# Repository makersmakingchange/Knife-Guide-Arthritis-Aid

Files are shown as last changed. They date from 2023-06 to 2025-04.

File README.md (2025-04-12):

# Knife Guide Arthritis Aid
The Knife Guide Arthritis Aid is a handle that attached to the back of a knife that allows a user to use both hands and requires less grip strength for the same amount of control. It is designed for users with arthritis that have difficulty gripping the handles of knives.

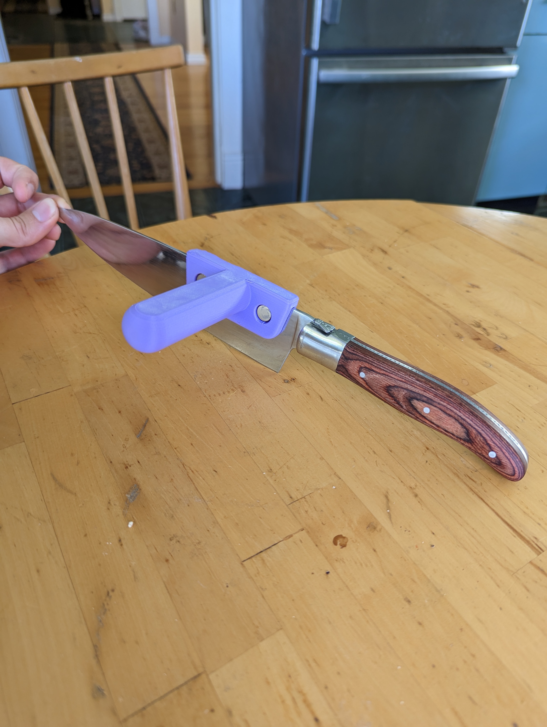
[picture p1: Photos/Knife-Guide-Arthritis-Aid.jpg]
Picture of Knife Guide Arthritis Aid.


## More info at
- [Makers Making Change Project Page](https://makersmakingchange.com/project/knife-guide-arthritis-aid/)

## How to Obtain a Knife Guide Arthritis Aid
### 1. Do it Yourself (DIY) or Do it Together (DIT)

This is an open-source assistive technology, so anyone is free to build it. All of the files and instructions required to build the Knife Guide Arthritis Aid are contained within this repository. Refer to the Maker Checklist below.

### 2. Request a build of this device

If you would like to obtain a Knife Guide Arthritis Aid, you may submit a build request through the [MMC Library Page](https://makersmakingchange.com/project/knife-guide-arthritis-aid/). The requestor is responsible for the cost of materials and any shipping.

### 3. How to build this device for someone else

If you have the skills and equipment to build this device, and would like to donate your time to create the switch for someone who needs it, visit the [MMC Maker Wanted](https://makersmakingchange.com/maker-wanted/) section.

## Getting Started

### 1. Read the Makers Checklist

The Makers Checklist 

### 2. Order the Off-The-Shelf Components

The [Bill of Materials](/Documentation/Knife_Guide_Arthritis_Aid_BOM_V1.0.xlsx) lists all of the parts and components required to build the Knife Guide Arthritis Aid. The of the off-the-shelf components are online or may be available in smaller quantities at your local hardware store or dollar store.

### 3. Print the 3D Printable components

Print the components

All of the files and individual print files can be in the [/Build_Files/3D_Printing_Files](/Build_Files/3D_Printing_Files/) folder.

### 4. Assemble the Knife Guide Arthritis Aid

Reference the [Assembly Guide](/Documentation/Knife_Guide_Arthritis_Aid_Assembly_Guide_V1.0.pdf) for the tools and steps required to build each portion.

## Files
### Documentation
| Document             | Version | Link |
|----------------------|---------|------|
| Design Rationale     | 1.0     | [Knife_Guide_Arthritis_Aid_Design_Rationale](/Documentation/Knife_Guide_Arthritis_Aid_Design_Rationale_V1.0.pdf)     |
| Maker Checklist      | 1.0     | [Knife_Guide_Arthritis_Aid_Maker_Checklist](/Documentation/Knife_Guide_Arthritis_Aid_Maker_Checklist_V1.0.pdf)     |
| Bill of Materials    | 1.0     | [Knife_Guide_Arthritis_Aid_Bill_of_Materials](/Documentation/Knife_Guide_Arthritis_Aid_BOM_V1.0.xlsx)     |
| 3D Printing Guide    | 1.0     | [Knife_Guide_Arthritis_Aid_3D_Printing_Guide](/Documentation/Knife_Guide_Arthritis_Aid_3D_Printing_Guide_V1.0.pdf)     |
| Assembly Guide       | 1.0     | [Knife_Guide_Arthritis_Aid_Assembly_Guide](/Documentation/Knife_Guide_Arthritis_Aid_Assembly_Guide_V1.0.pdf)     |
| User Guide           | 1.0     | [Knife_Guide_Arthritis_Aid_User_Guide](/Documentation/Knife_Guide_Arthritis_Aid_User_Guide_V1.0.pdf)    |
| Changelog            | 1.0     | [Knife_Guide_Arthritis_Aid_Changelog](/Documentation/Knife_Guide_Arthritis_Aid_Changelog_V1.0.pdf)     |

### Design Files
 - [CAD Files](/Design_Files)

### Build Files
 - [3D Printing Files](/Build_Files/3D_Printing_Files)

## Attribution
Designers:
 - Initial design by [Christopher Thormodson](https://www.myminifactory.com/users/cjthormodson)
 - Update design and documentation by Neil Squire Society / Makers Making Change. 

## License
Everything needed or used to design, make, test, or prepare the Knife Guide Arthritis Aid is licensed under the [MyMiniFactory - Credit - Remix - Noncommercial](https://www.myminifactory.com/object-licensing).

Accompanying material such as instruction manuals, videos, and other copyrightable works that are useful but not necessary to design, make, test, or prepare the Knife Guide Arthritis Aid are published under a Creative Commons Attribution-ShareAlike 4.0 license https://creativecommons.org/licenses/by-sa/4.0/ (CC BY-SA 4.0).

----

<!-- ABOUT MMC START -->
## About Makers Making Change
[Makers Making Change Logo](https://www.makersmakingchange.com/)

Makers Making Change is a program of [Neil Squire](https://www.neilsquire.ca/), a Canadian non-profit that uses technology, knowledge, and passion to empower people with disabilities.

Makers Making Change leverages the capacity of community based Makers, Disability Professionals and Volunteers to develop and deliver affordable Open Source Assistive Technologies.

 - Website: [www.MakersMakingChange.com](https://www.makersmakingchange.com/)
 - GitHub: [makersmakingchange](https://github.com/makersmakingchange)
 - Bluesky: [@makersmakingchange.bsky.social](https://bsky.app/profile/makersmakingchange.bsky.social)
 - Instagram: [@makersmakingchange](https://www.instagram.com/makersmakingchange)
 - Facebook: [makersmakechange](https://www.facebook.com/makersmakechange)
 - LinkedIn: [Neil Squire Society](https://www.linkedin.com/company/neil-squire-society/)
 - Thingiverse: [makersmakingchange](https://www.thingiverse.com/makersmakingchange/about)
 - Printables: [MakersMakingChange](https://www.printables.com/@MakersMakingChange)

### Contact Us
For technical questions, to get involved, or to share your experience we encourage you to [visit our website](https://www.makersmakingchange.com/) or [contact us](https://www.makersmakingchange.com/s/contact).
<!-- ABOUT MMC END -->

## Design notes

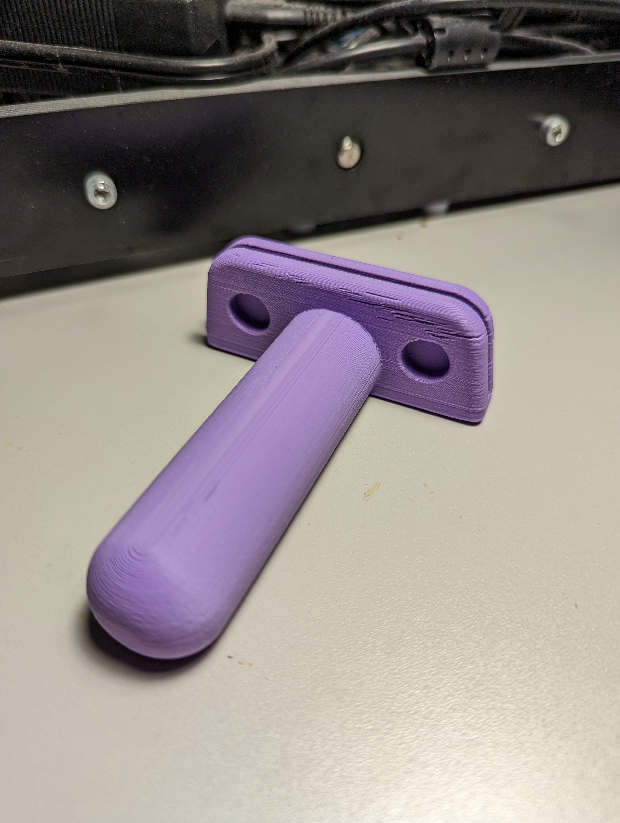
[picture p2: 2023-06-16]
Photos/One_Piece_Handle.jpg

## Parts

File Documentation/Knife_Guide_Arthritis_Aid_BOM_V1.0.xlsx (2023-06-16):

Device: xxxxx |  | Total Cost | Total Print time (hr) | Total filament (g)
Version: V1.0 | Date Created: 4/20/2021 | $1.93 | 3.37 | 27
Commercial Parts:
Part type (Electrical. Mechanical, Sanitization, ect) | Part Name | Quantity Needed | Pkg Quantity | Price per package | Price per Unit | Price for qty needed | Link
Mechanical | Magnet 15mmx3mm | 4 | 60 | $18.77 | $0.31 | $1.25 | https://www.amazon.ca/dp/B09DYG7GLW?psc=1&ref=ppx_yo2ov_dt_b_product_details
 |  |  |  |  |  | $0.00
 |  |  |  |  |  | $0.00
3D Printed Parts ESTIMATED PRICING USING 1KG ROLL COST: | $25.00
Part | Description | Quantity Needed | TOTAL Mass (g) | Estimated Price | Print Time (Min) | Link
One_Piece_Handle.stl | The main device handle | 1 | 27 | $0.68 | 202
 |  |  |  | $0.00
 |  |  |  | $0.00
 |  |  |  | $0.00
 |  |  |  | $0.00
 |  |  | Total Print Cost: | $0.68
Tools for Assembly
Superglue
Alternatives (if there are other sources for some parts link them below)
Part and description | Link

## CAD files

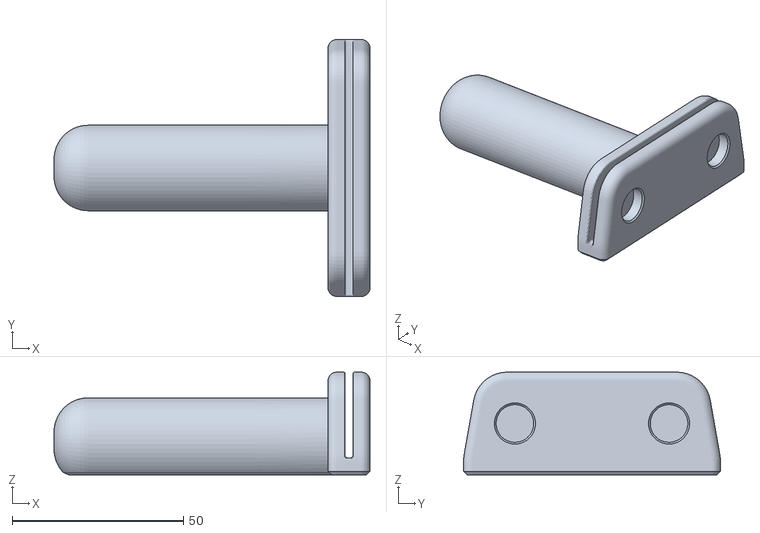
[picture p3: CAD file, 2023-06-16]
Build_Files/3D_Printing_Files/One_Piece_Handle.stl
92.2 x 75.0 x 30.0

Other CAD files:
Design_Files/One Piece Handle v3.f3d

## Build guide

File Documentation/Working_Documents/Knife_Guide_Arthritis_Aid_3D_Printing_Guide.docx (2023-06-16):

# 3D Printing Summary

Metrics
Total Print Time (min) | 202
Total Number of Components | 1
Typical Total Mass (g) | 27
Typical Number of Print Setups | 1

# 3D Printing Settings

Print File Name | Qty | Total Print Time (hr:min) | Mass (g) | Infill (%) | Support(Y/N) | Layer Height/ Nozzle Diameter(mm) | Notes (orientation, special settings, etc.)
One_Piece_Handle.stl | 1 | 3:22 | 27 | 20 | N | 0.2/0.4 | - Print in orientation given in STL

# Customization Options

- The device can be printed in any colour the user would like
- The width of the knife channel can be changed in the Fusion 360 file

# Examples of Quality Prints

Photos of One_Piece_Handle

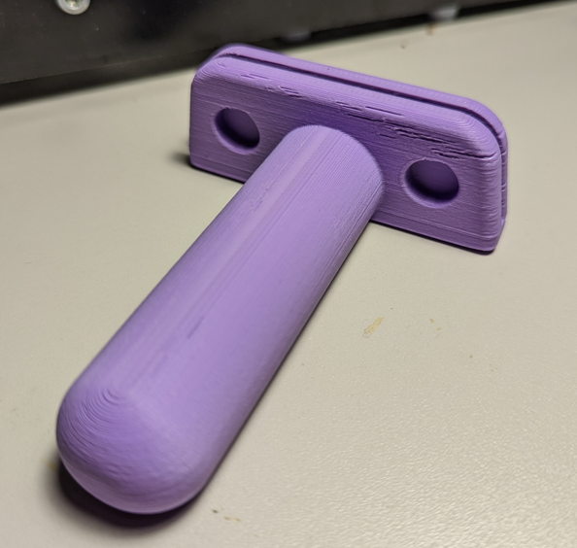
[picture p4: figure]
The one piece handle printed in purple

© 2023 by Neil Squire. This work is licensed under the CC BY SA 4.0 License: http://creativecommons.org/licenses/by-sa/4.0 Files available at https://makersmakingchange.com/project/knife-guide-arthritis-aid/ Page 1 of 2

V1.0 | March 2023 Knife Guide Arthritis Aid 3D Printing Guide

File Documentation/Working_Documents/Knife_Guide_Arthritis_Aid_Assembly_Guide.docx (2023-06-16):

# Required Components

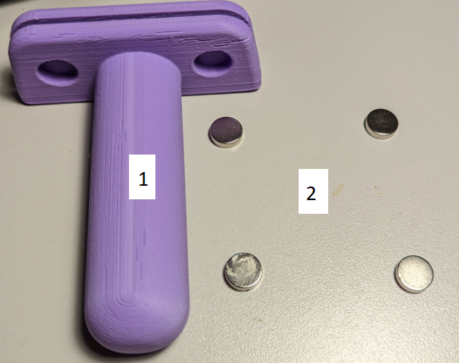
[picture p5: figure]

| BOM 1. One_Piece_Handle.stl x1 2. Magnet x4

# Required Tools

- Gorilla Glue

# Required Personal Protective Equipment (PPE)

- Safety glasses

# Assembly Instructions

## Step 1

Take 4 magnets and place them into the slots on the 3D printed handle. The magnets will hold themselves in place. Using a pea sized amount of gorilla glue, secure the magnets in place so they cannot be removed.

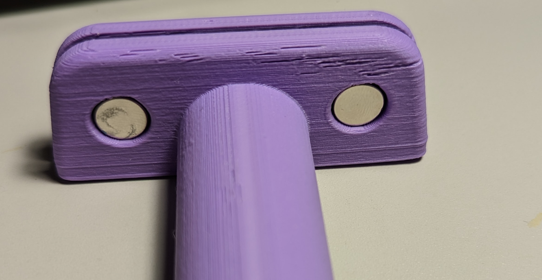
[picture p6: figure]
Printed device with the magnets installed

## Step 2

Place the assembled handle over the spine of the knife to complete the build.

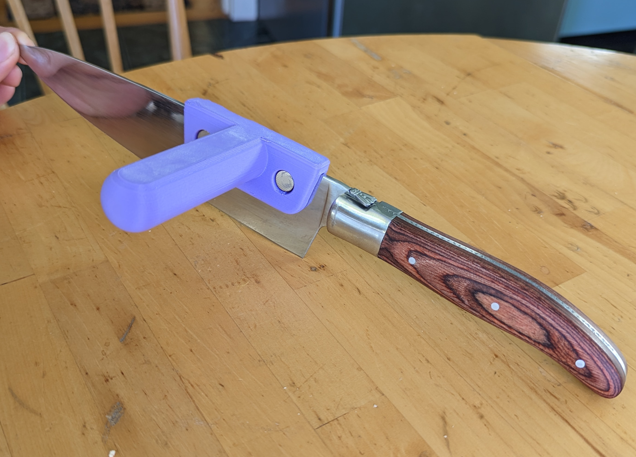
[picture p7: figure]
A chefs knife with the assembled device sitting on the spine of the knife, near the handle

© 2023 by Neil Squire. This work is licensed under the CC BY SA 4.0 License: http://creativecommons.org/licenses/by-sa/4.0 Files available at https://makersmakingchange.com/project/knife-guide-arthritis-aid/ Page 1 of 1

V1.0 | March 2023 Knife Guide Arthritis Aid Assembly Guide

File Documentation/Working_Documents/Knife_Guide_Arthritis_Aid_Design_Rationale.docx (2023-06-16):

# Introduction

The Knife Guide Arthritis Aid is a handle that attached to the back of a knife that allows a user to use both hands and requires less grip strength for the same amount of control. It is designed for users with arthritis that have difficulty gripping the handles of knives.

# Research

Name | Image | Price | Link

Commercial

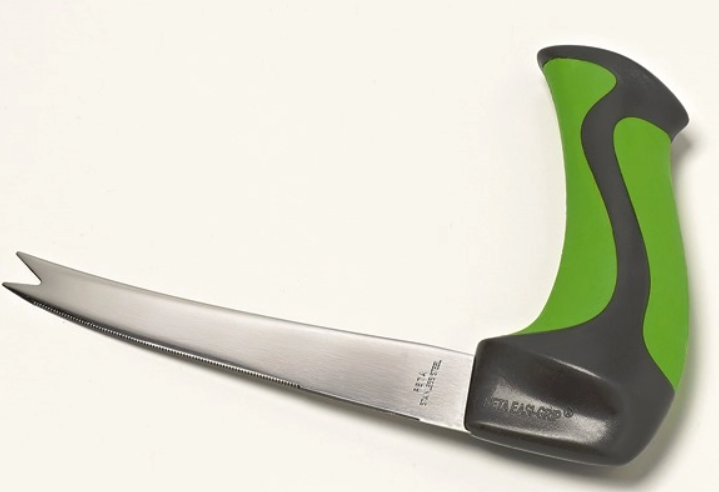
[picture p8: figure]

Easi-Grip Arthritis Fork Knife | | $17.95 | Link (https://www.arthritissupplies.com/easi-grip-arthritis-fork-knife.html)

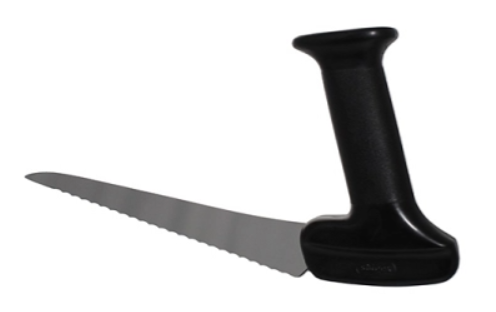
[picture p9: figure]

Swedish Serrated Knife | | $45.95 | Link (https://www.arthritissupplies.com/swedish-serrated-knife.html)

DIY

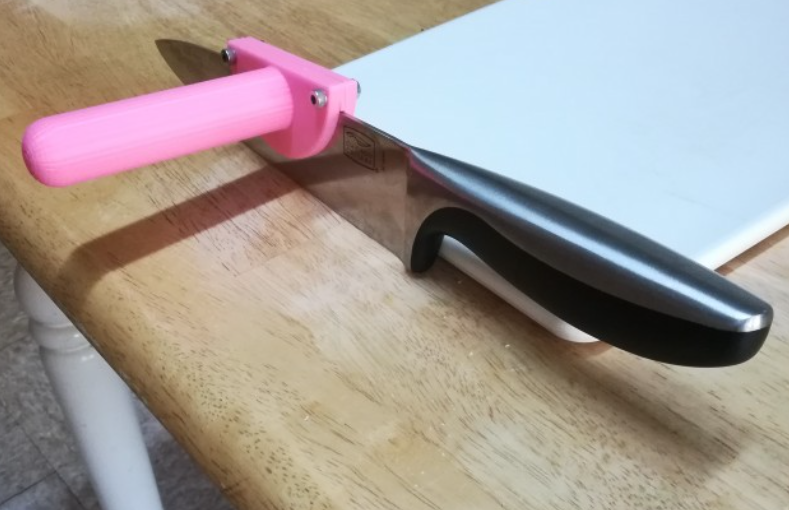
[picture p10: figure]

3D Printable Knife Guide Arthritis Aid | | N/A | Link (https://www.myminifactory.com/object/3d-print-knife-guide-arthritis-aid-77506)

# Requirements

## Goals

G01 | Create a handle that allows arthritis uses to use a knife

## Functional Requirements

F01 | Device must firmly hold onto the knife
F02 | Device must have a more natural grip position
F03 | Device must not block use of the knife

## Constraints

C01 | Device must be printed in one piece with no supports

# Prototyping

Version 1: Original Design

- Two flat plates with a spacer between them, connected by two bolts with a handle on one plate
- When the screws are tightened, the plates angle and separate at the bottom, preventing them from gripping the blade

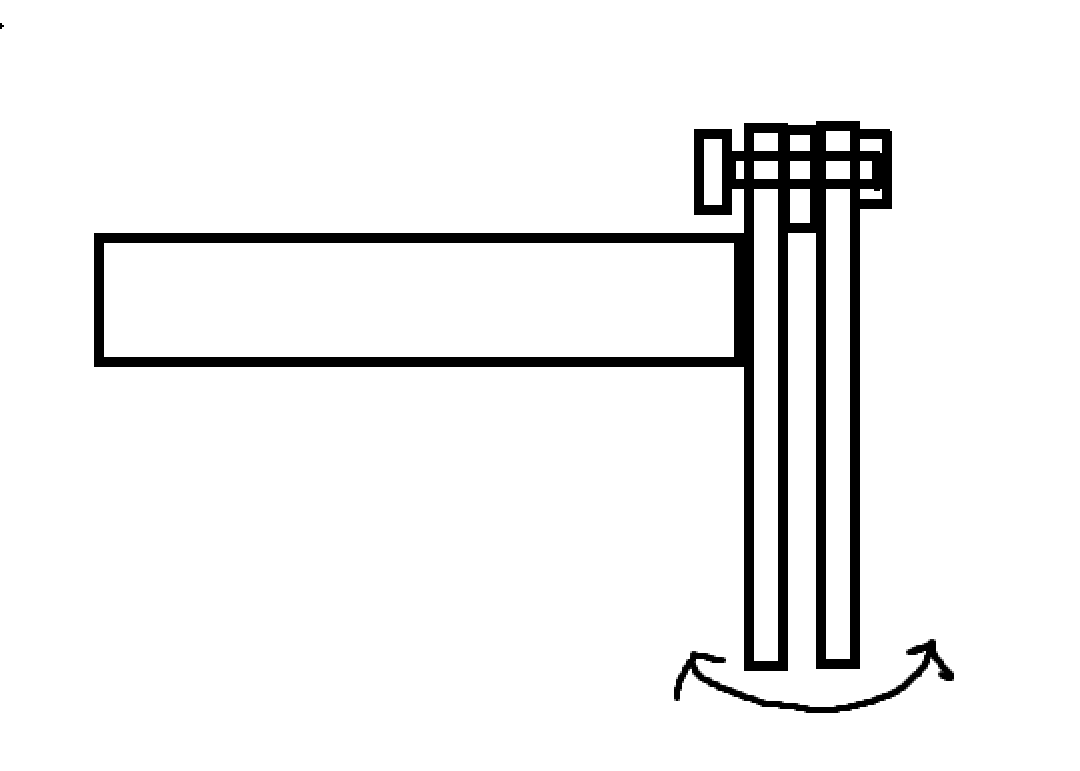
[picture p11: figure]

Version 2: Modified Design

- The plates were modified so they had a taper that would keep the plates parallel after the screws are tightened
- The plates still were loose after the screws were tightened

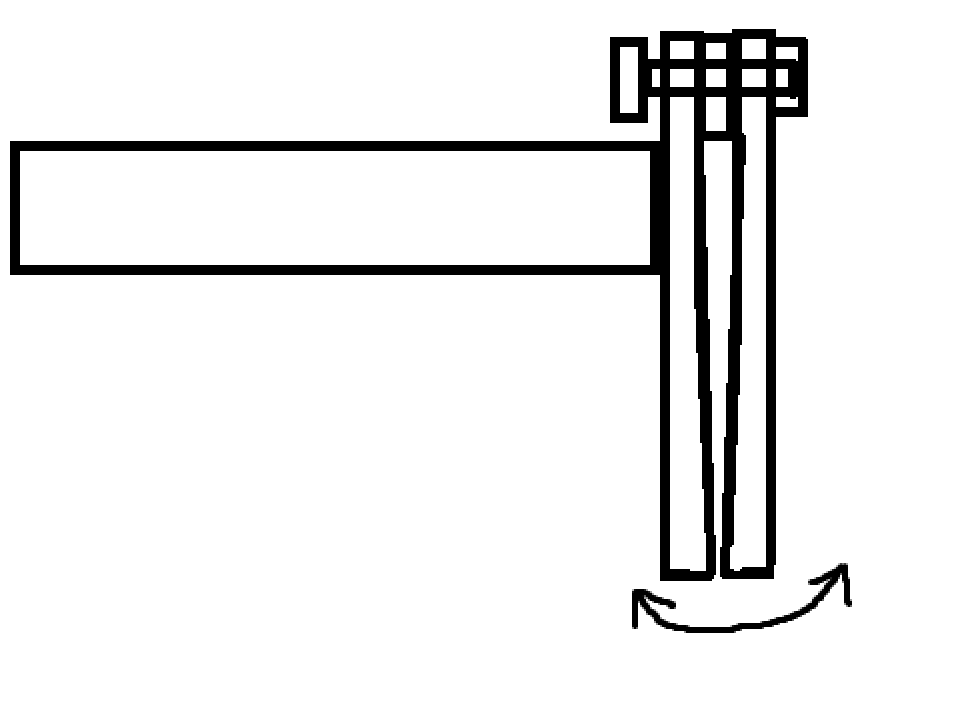
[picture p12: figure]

Version 3: Magnet Design

- One piece print in place design
- Pockets for magnets to be inserted on the outside
- Knife thickness is a parametric variable that can be changed
- Most force is on the downstroke, the magnets keep the handle on the knife on the upstroke, but not expected to have to bear significant force
- Covers much less of the blade, allowing it to be used on non-chef knives

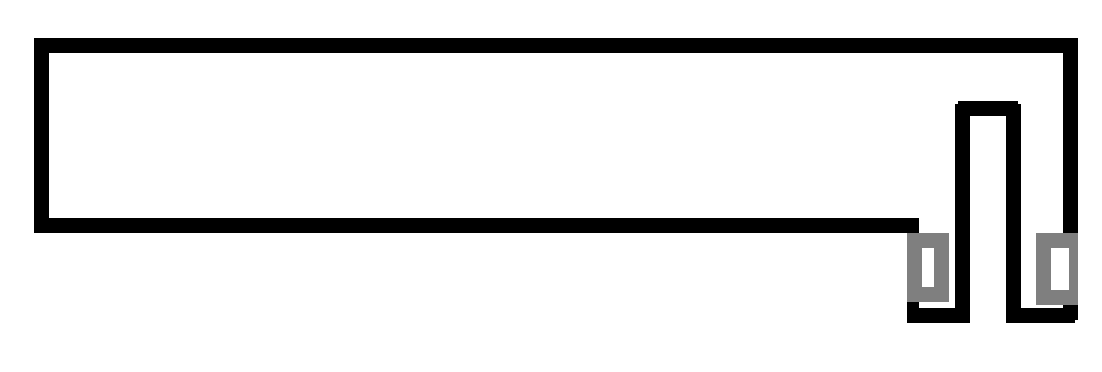
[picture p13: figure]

# Testing

After assembling the final magnet version, it was found to stay on the knife well, and it left a usable amount of the knife exposed. Gorilla glue was chosen as the glue, since it is food safe, as well as being less brittle to resist the shock of being dropped.

# Opportunities for Improvement

The handle could be rotated 90 degrees to be vertical, as seen on some commercial arthritis knives.

© 2023 by Neil Squire. This work is licensed under the CC BY SA 4.0 License: http://creativecommons.org/licenses/by-sa/4.0 Files available at https://makersmakingchange.com/project/knife-guide-arthritis-aid/ Page 1 of 1

V1.0 | March 2023 Knife Guide Arthritis Aid Design Rationale

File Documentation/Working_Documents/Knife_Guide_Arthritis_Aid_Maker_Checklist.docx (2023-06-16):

# Maker To Do List

- Read through the Assembly Guide to become familiar with required components, tools, supplies, and safety gear and overall assembly steps.
- Talk to User about customization options (e.g., color, any special requests, etc.)
- Order hardware components
- Gather tools, supplies, and safety equipment.
- Assemble the device
- Test device
- Print “User Quick Guide”

# Items to Give to User

- Assembled, tested device
- “User Quick Guide”

© 2023 by Neil Squire. This work is licensed under the CC BY SA 4.0 License: http://creativecommons.org/licenses/by-sa/4.0 Files available at https://makersmakingchange.com/project/knife-guide-arthritis-aid/ Page 1 of 1

V1.0 | March 2023 Knife Guide Arthritis Aid Maker Checklist

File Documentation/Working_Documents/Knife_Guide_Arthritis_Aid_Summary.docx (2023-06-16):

# Title

Knife Guide Arthritis Aid

## Subtitle

The Knife Guide Arthritis Aid is a handle that attached to the back of a knife that allows a user to use both hands and requires less grip strength for the same amount of control.

## Device Details

### Overview

The Knife Guide Arthritis Aid is a handle that attached to the back of a knife that allows a user to use both hands and requires less grip strength for the same amount of control. It is designed for users with arthritis that have difficulty gripping the handles of knives.

### Usage

To use, place the device over the back of the knife. The new handle can now be gripped at a more natural angle than the original handle, and the knife used as normal. However, at least one hand must remain on the original handle during use. Attempting to hold the knife with just the new handle could cause the knife to fall out of the handle.

### Cost

<$5

### Build Instructions

<Summary of build – off-the shelf parts? Custom PCB? 3D Printing? Programming?

#### Skills Required

- 3D printing

#### Time Required

3D printing time: 3h 22min

Assembly Time: 5 min

#### Tools

- 3D printer
- Superglue

#### Components

- 1x One_Piece_Handle.stl
- 4x magnet

### Attribution

- Initial design by Christopher Thormodson @cjthormodson - MyMiniFactory (https://www.myminifactory.com/users/cjthormodson)
- Revisions and documentation by Neil Squire Society/Makers Making Change

© 2023 by Neil Squire. This work is licensed under the CC BY SA 4.0 License: http://creativecommons.org/licenses/by-sa/4.0 Files available at https://makersmakingchange.com/project/knife-guide-arthritis-aid/ Page 1 of 1

V1.0 | March 2023 Knife Guide Arthritis Aid Summary

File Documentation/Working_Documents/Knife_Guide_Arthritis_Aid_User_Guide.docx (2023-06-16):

## Introduction

The Knife Guide Arthritis Aid is a handle that attaches to the back of a knife that allows a user to use both hands while cutting and requires less grip strength for the same amount of control.

## Features

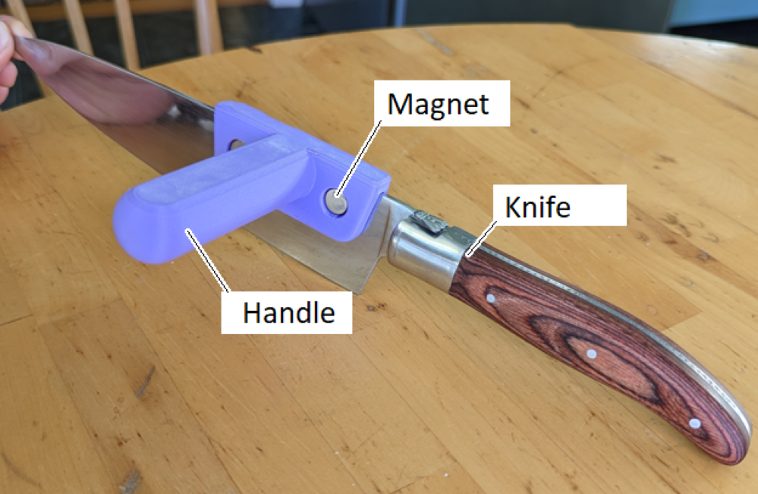
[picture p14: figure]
A labeled photo of a chefs knife with the assembled device attached

## Usage

To use, place the device over the back of the knife. The new handle can now be gripped at a more natural angle than the original handle, and the knife used as normal. However, at least one hand must remain on the original handle during use. Attempting to hold the knife with just the new handle could cause the knife to fall out of the handle.

## Compatibility

The device is compatible with any magnetic knife with a blade height of more than 3cm. The provided stl is designed for a knife with a blade thickness of 2.25mm, but the thickness can be adjusted in the provided Fusion 360 file.

## Specifications

Device weight: 31g

Handle diameter: 25mm

Length: 95mm

Width: 75mm

Slot depth: 30mm

Slot width: 2.25mm

## Cleaning

The device can be wiped clean with a damp cloth.

© 2023 by Neil Squire. This work is licensed under the CC BY SA 4.0 License: http://creativecommons.org/licenses/by-sa/4.0 Files available at https://makersmakingchange.com/project/knife-guide-arthritis-aid/ Page 2 of 3

V1.0 | March 2023 Knife Guide Arthritis Aid user Quick Guide

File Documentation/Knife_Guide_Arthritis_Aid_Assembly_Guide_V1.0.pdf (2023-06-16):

V1.0 | March 2023

# Knife Guide Arthritis Aid

# ASSEMBLY GUIDE

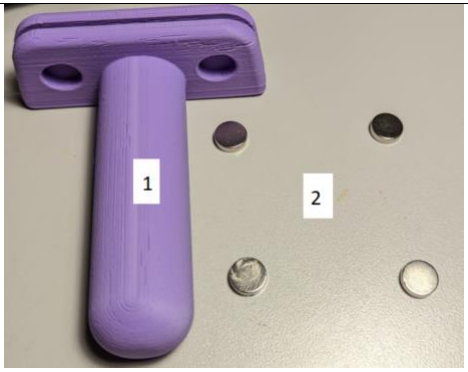
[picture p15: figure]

© 2023 by Neil Squire. (https://neilsquire.ca/)
This work is licensed under the CC BY SA 4.0 License: http://creativecommons.org/licenses/by-sa/4.0
Files available at https://makersmakingchange.com/project/knife-guide-arthritis-aid/ | Page 1 of 2

# Required Components

## BOM 1. One_Piece_Handle.stl

x1

## 2. Magnet x4

# Required Tools

## - Gorilla Glue

# Required Personal Protective Equipment (PPE)

## - Safety glasses

# Knife Guide Arthritis Aid

# ASSEMBLY GUIDE

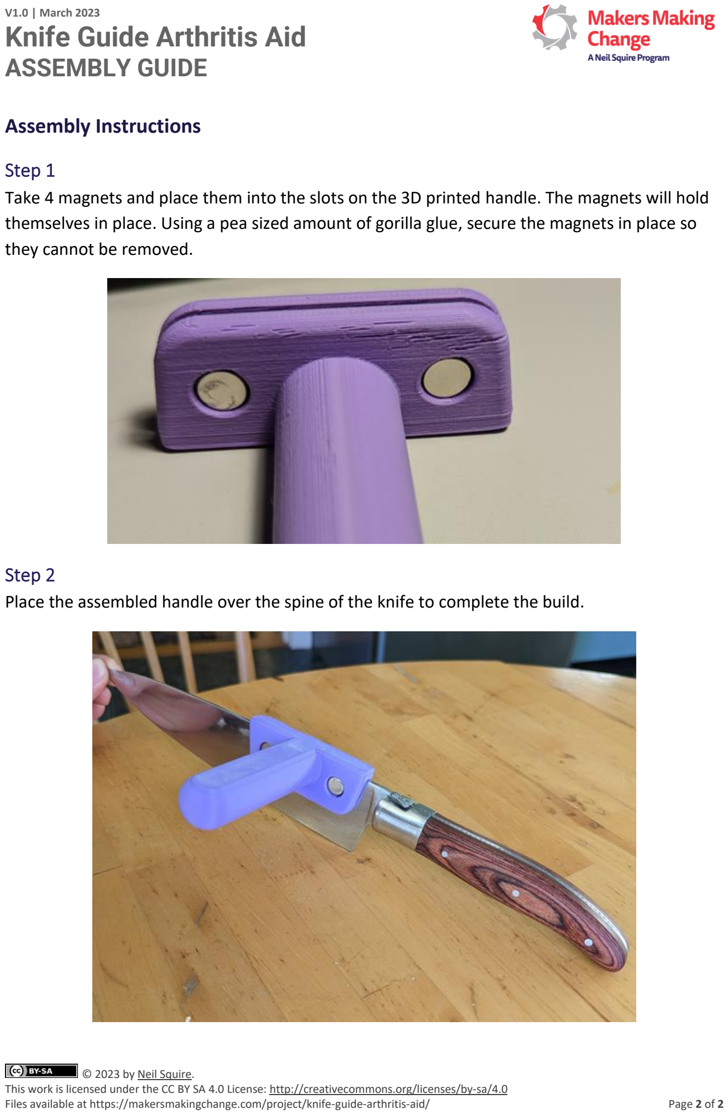
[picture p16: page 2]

V1.0 | March 2023

© 2023 by Neil Squire. (https://neilsquire.ca/)
This work is licensed under the CC BY SA 4.0 License: http://creativecommons.org/licenses/by-sa/4.0
Files available at https://makersmakingchange.com/project/knife-guide-arthritis-aid/ | Page 2 of 2

# Assembly Instructions

## Step 1

Take 4 magnets and place them into the slots on the 3D printed handle. The magnets will hold themselves in place. Using a pea sized amount of gorilla glue, secure the magnets in place so they cannot be removed.

## Step 2

Place the assembled handle over the spine of the knife to complete the build.

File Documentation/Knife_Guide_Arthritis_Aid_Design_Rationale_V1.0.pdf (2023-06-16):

V1.0 | March 2023

## Knife Guide Arthritis Aid

## DESIGN RATIONALE

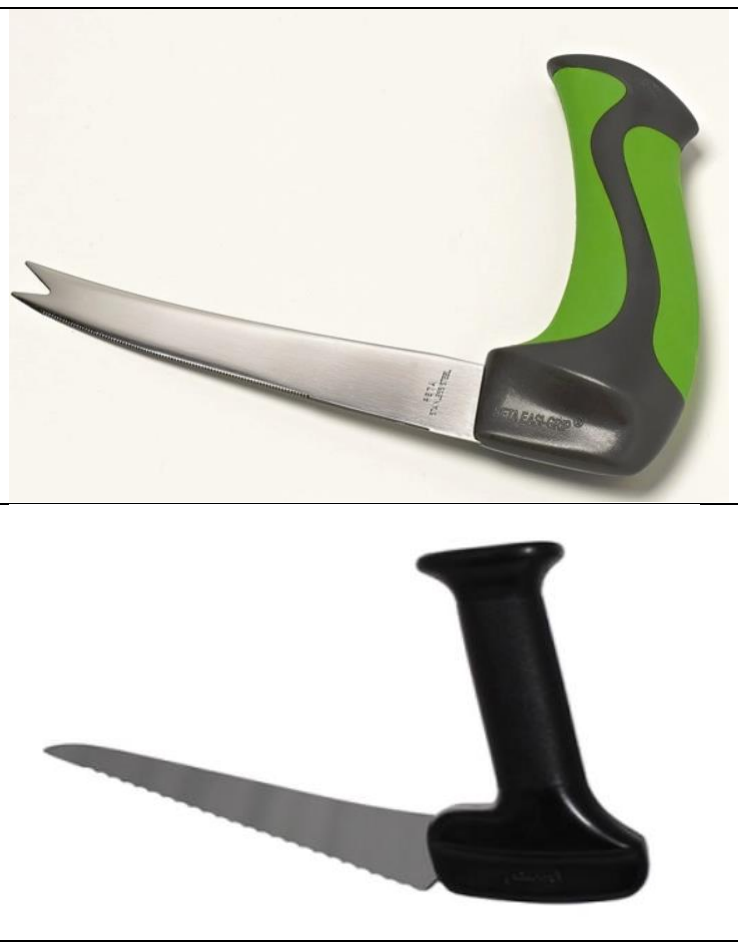
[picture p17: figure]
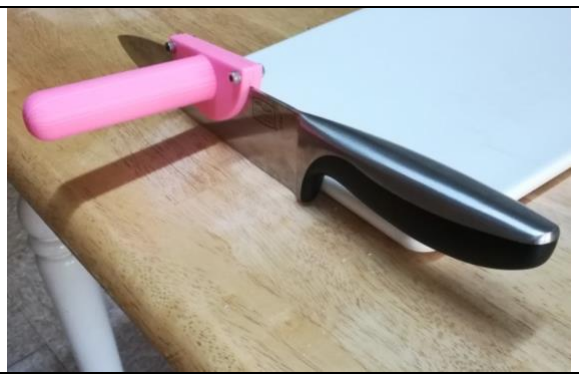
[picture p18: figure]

© 2023 by Neil Squire. (https://neilsquire.ca/)
This work is licensed under the CC BY SA 4.0 License: http://creativecommons.org/licenses/by-sa/4.0
Files available at https://makersmakingchange.com/project/knife-guide-arthritis-aid/ | Page 1 of 3

### Introduction

The Knife Guide Arthritis Aid is a handle that attached to the back of a knife that allows a user to use both hands and requires less grip strength for the same amount of control. It is designed for users with arthritis that have difficulty gripping the handles of knives.

### Research

Name | Image | Price | Link
Commercial
Easi-Grip Arthritis Fork Knife | $17.95 | Link (https://www.arthritissupplies.com/easi-grip-arthritis-fork-knife.html)
Swedish Serrated Knife | $45.95 | Link (https://www.arthritissupplies.com/swedish-serrated-knife.html)

DIY
3D Printable
Knife Guide
Arthritis Aid
N/A | Link (https://www.myminifactory.com/object/3d-print-knife-guide-arthritis-aid-77506)

## DESIGN RATIONALE

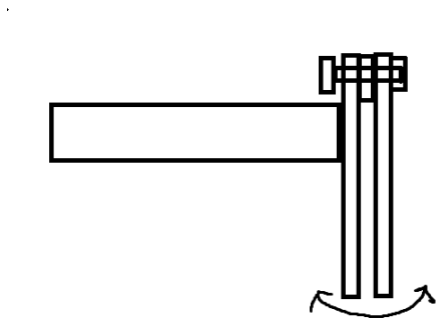
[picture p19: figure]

Files available at https://makersmakingchange.com/project/knife-guide-arthritis-aid/ | Page 2 of 3

### Requirements

### Goals

G01 Create a handle that allows arthritis uses to use a knife

### Functional Requirements

F01 | Device must firmly hold onto the knife
F02 | Device must have a more natural grip position
F03 | Device must not block use of the knife

### Constraints

C01 Device must be printed in one piece with no supports

### Prototyping

Version 1: Original Design

- Two flat plates with a spacer between them, connected by two bolts with a handle on one plate
- When the screws are tightened, the plates angle and separate at the bottom, preventing them
| from gripping the blade

Version 2: Modified Design

- The plates were modified so they had a taper that would keep the plates parallel after the screws are tightened
- The plates still were loose after the screws were tightened

## DESIGN RATIONALE

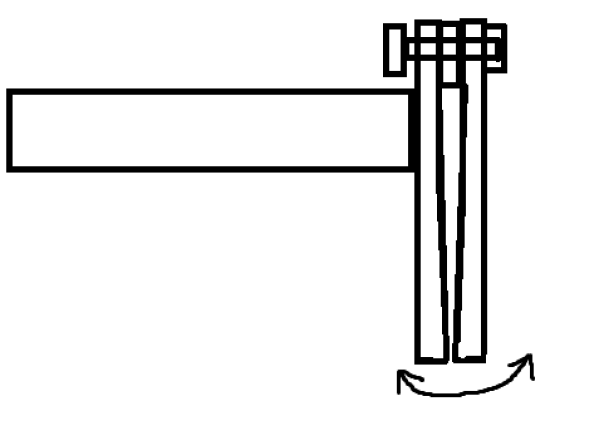
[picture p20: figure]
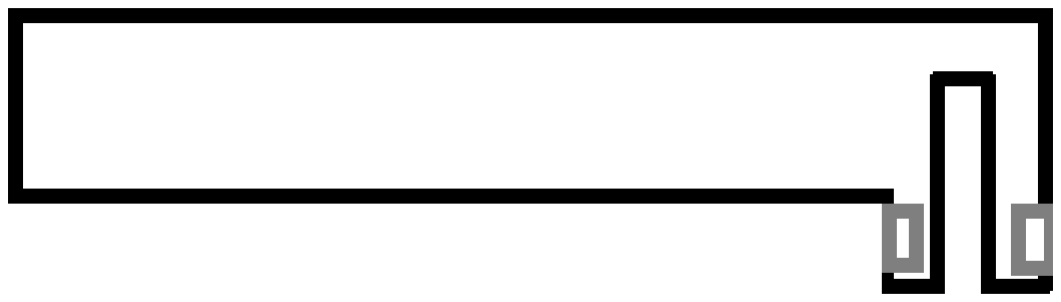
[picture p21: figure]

Files available at https://makersmakingchange.com/project/knife-guide-arthritis-aid/ | Page 3 of 3

Version 3: Magnet Design

- One piece print in place design
- Pockets for magnets to be inserted on the outside
- Knife thickness is a parametric variable that can be changed
- Most force is on the downstroke, the magnets keep the handle on the knife on the upstroke, but not expected to have to bear significant force
- Covers much less of the blade, allowing it to be used on non-chef knives

### Testing

After assembling the final magnet version, it was found to stay on the knife well, and it left a usable amount of the knife exposed. Gorilla glue was chosen as the glue, since it is food safe, as well as being less brittle to resist the shock of being dropped.

### Opportunities for Improvement

The handle could be rotated 90 degrees to be vertical, as seen on some commercial arthritis knives.

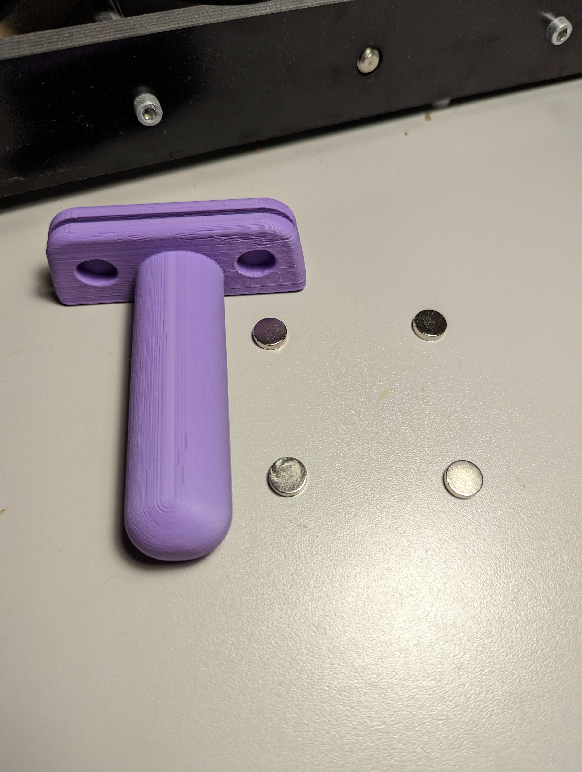
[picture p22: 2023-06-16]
Photos/Assembly Layout.jpg

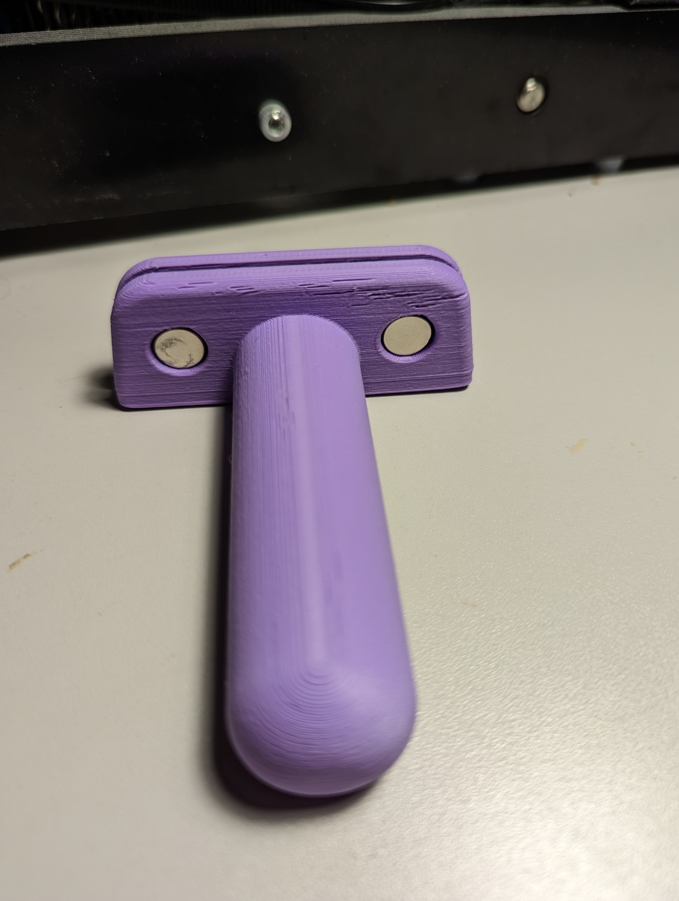
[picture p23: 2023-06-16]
Photos/Assembly Step 1.jpg
